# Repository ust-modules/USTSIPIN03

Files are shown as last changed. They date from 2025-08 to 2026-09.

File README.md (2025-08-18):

## USTSIPIN03 - Semiconductor-based ionizing radiation dosimeter and spectrometer analog front-end

The USTSIPIN03 is developed as a single-board improved variant of the [PIND02](https://github.com/mlab-modules/PIND02) and [PCRD07](https://github.com/mlab-modules/PCRD07) modules from the [MLAB.cz development system](https://www.mlab.cz/). The analog front-end is the sensing component of the [AIRDOS04 cosmic radiation detector and dosimeter](https://docs.dos.ust.cz/airdos/AIRDOS04).

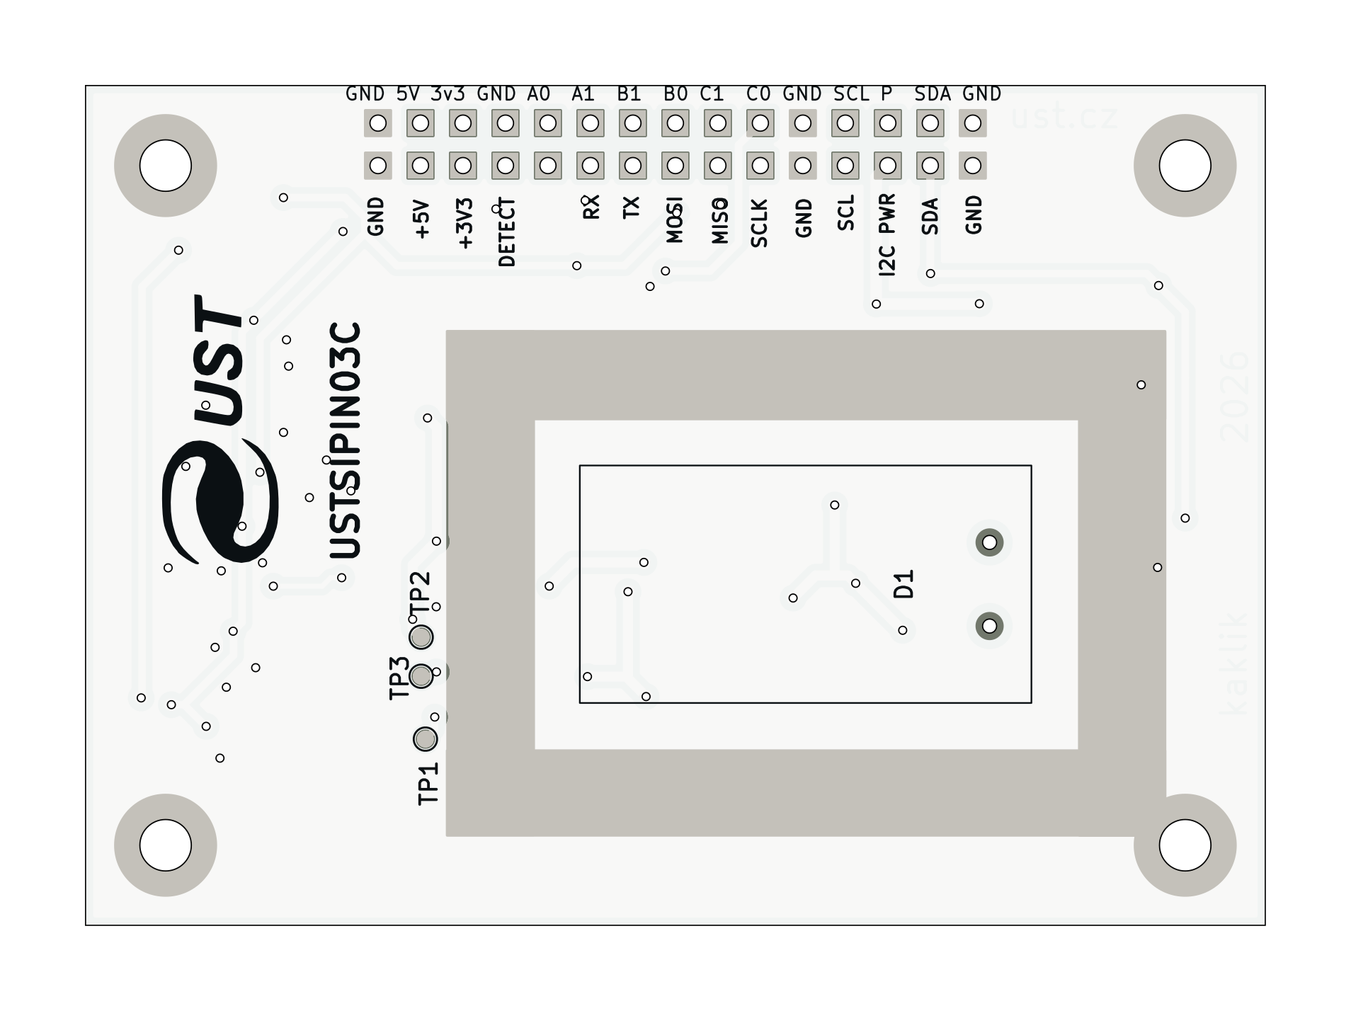
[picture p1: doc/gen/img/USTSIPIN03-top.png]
USTSIPIN03 Top view


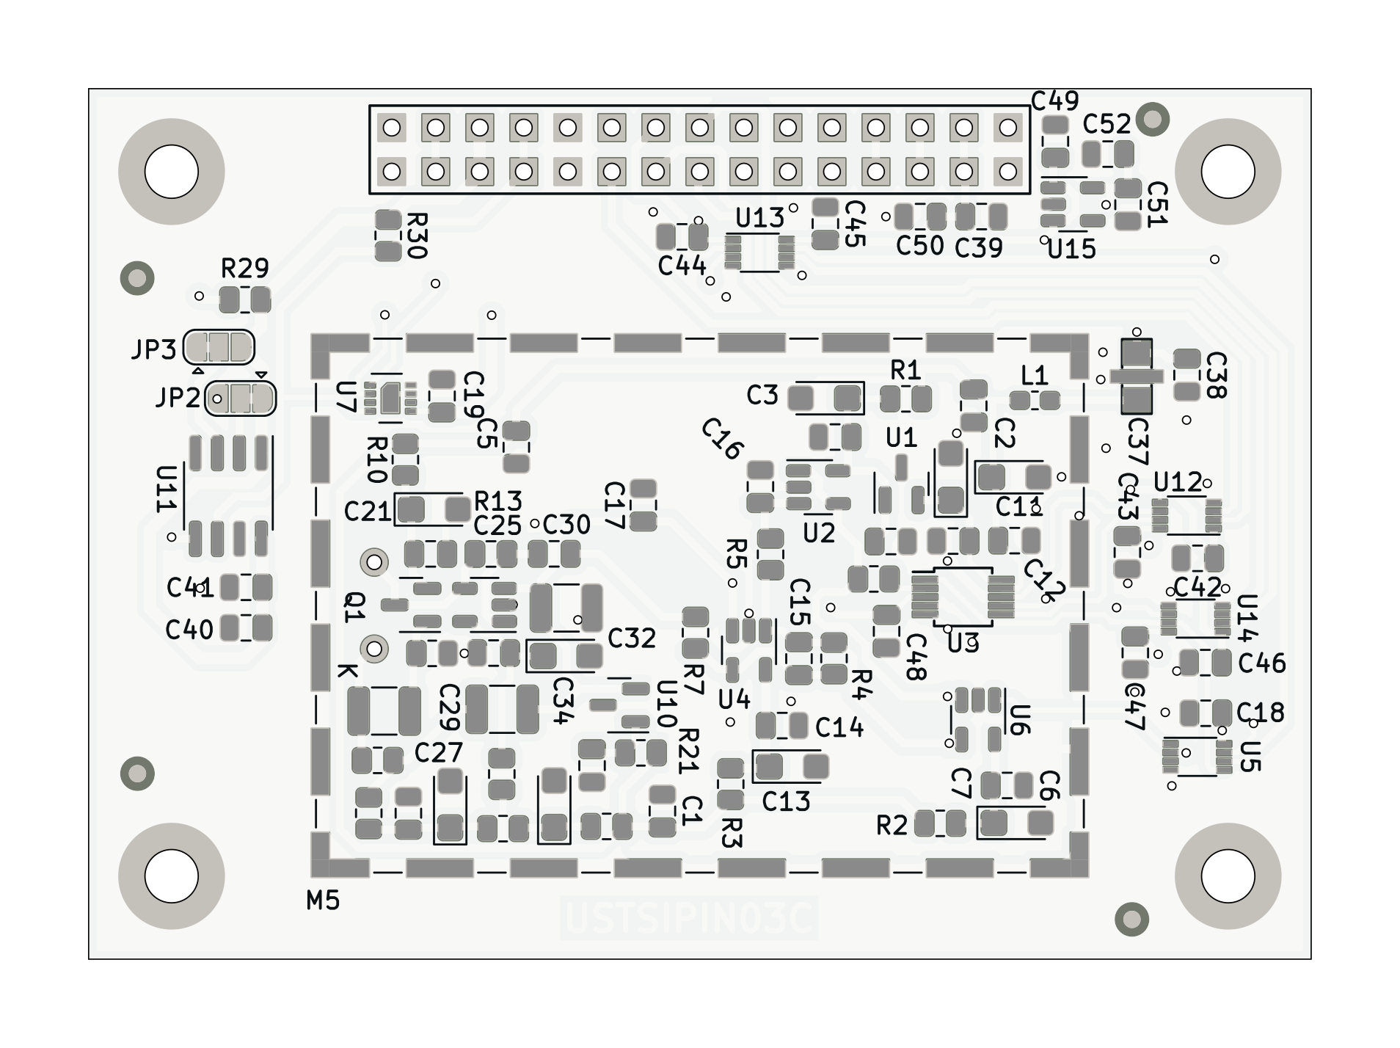
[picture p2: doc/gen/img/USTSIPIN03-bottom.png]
USTSIPIN03 Bottom view


### Features

* High-sensitivity silicon semiconductor PIN diode detector front-end
* Low-noise analog signal chain optimized for wide-energy radiation detection
* Designed for spectrometric and dosimetric measurements
* Suitable for connection to system MCU or FPGA via SPI interface
* Auxiliary I2C interface for service and calibration data access

### Electrical and Interface Specifications

* **Power supply**: +5 V DC
* **Maximum power consumption**: 5.5 mA (28 mW)
* **Main data interface**: SPI with up to 15 MHz system clock
* **Service interface**: I2C with access to
    * Temperature and humidity sensors
    * Unique serial number
    * Calibration memory
* Dimensions: 70.65 x 50.3 x 10 mm
* Mass: 24 g (including connector) 

AIRDOS04 Sensor Top

AIRDOS04 Sensor Bottom

### Measurement Specifications

* **Detection element**: Silicon PIN diode, volume 44 mm³
* **Effective number of energy channels**: ~65000
* **Deposited energy range**: 40 keV to 80 MeV
* **Spectral resolution**: 15 ±2 keV
* **Maximum sampling rate**: 250 kHz
* **Measurement modes**:
  * Pulse counting
  * Deposited energy spectroscopy
  * Dose rate estimation

### Applications

* Cosmic ray detection
* Environmental radiation monitoring
* Portable dosimetry systems
* Radiation protection systems
  
### Related Projects

* [AIRDOS04](https://github.com/UniversalScientificTechnologies/AIRDOS04) - Complete radiation detection system based on USTSIPIN03
* [PIND02](https://github.com/mlab-modules/PIND02) - Predecessor MLAB module
* [PCRD07](https://github.com/mlab-modules/PCRD07) - Related MLAB analog front-end module

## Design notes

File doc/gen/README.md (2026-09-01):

# PCB

Board size: 70.61x50.29 mm (2.78x1.98 inches)

- This is the size of the rectangle that contains the board
- Thickness: 1.6 mm (63 mils)
- Material: FR4
- Finish: HAL SnPb
- Layers: 2
- Copper thickness: 35 µm

Solder mask: TOP / BOTTOM

- Color: Green

Silk screen: TOP / BOTTOM

- Color: White

Stackup:

| Name                 | Type                 | Color            | Thickness [µm]| Material        | Er        | Loss tan     |
|----------------------|----------------------|------------------|---------------|-----------------|-----------|--------------|
| F.SilkS              | Top Silk Screen      |                  |               |                 |           |              |
| F.Mask               | Top Solder Mask      |                  |            10 |                 |           |              |
| F.Cu                 | copper               |                  |            35 |                 |           |              |
| dielectric 1         | core                 |                  |          1510 | FR4             |       4.5 |        0.020 |
| B.Cu                 | copper               |                  |            35 |                 |           |              |
| B.Mask               | Bottom Solder Mask   |                  |            10 |                 |           |              |
| B.Paste              | Bottom Solder Paste  |                  |               |                 |           |              |
| B.SilkS              | Bottom Silk Screen   |                  |               |                 |           |              |

# Important sizes

Clearance: 0.2 mm (8 mils)

Track width: 0.2 mm (8 mils)

- By design rules: 0.2 mm (8 mils)

Drill: 0.5 mm (20 mils)

- Vias: 0.5 mm (20 mils) [Design: 0.4 mm (16 mils)]
- Pads: 0.85 mm (33 mils)
- The above values are real drill sizes, they add 0.1 mm (4 mils) to plated holes (PTH)

Via: 0.8/0.4 mm (31/16 mils)

- By design rules: 0.8/0.3 mm (31/12 mils)
- Micro via: yes [0.2/0.1 mm (8/4 mils)]
- Buried/blind via: yes
- Total: 56 (thru: 56 buried/blind: 0 micro: 0)

Outer Annular Ring: 0.15 mm (6 mils)

- By design rules: 0.26 mm (10 mils)

Eurocircuits class: 4B
- Using min drill 0.5 mm for an OAR of 0.15 mm

# General stats

Components count: (SMD/THT)

- Top: 0/6 (THT)
- Bottom: 87/1 (SMD + THT)

Defined tracks:

- 0.2 mm (8 mils)
- 0.3 mm (12 mils)
- 0.4 mm (16 mils)
- 0.5 mm (20 mils)
- 0.6 mm (24 mils)
- 0.7 mm (28 mils)
- 0.8 mm (31 mils)

Used tracks:

- 0.2 mm (8 mils) (2) defined: yes
- 0.3 mm (12 mils) (136) defined: yes
- 0.4 mm (16 mils) (59) defined: yes
- 0.45 mm (18 mils) (415) defined: no
- 0.5 mm (20 mils) (4) defined: yes
- 0.6 mm (24 mils) (21) defined: yes
- 0.7 mm (28 mils) (37) defined: yes

Defined vias:

Used vias:

- 0.8/0.4 mm (31/16 mils) (Count: 56, Aspect: 2.0 A) defined: no

Holes (excluding vias):

- 0.76 mm (30 mils) (2)
- 0.89 mm (35 mils) (30)
- 3.0 mm (118 mils) (4)

Oval holes:

Drill tools (including vias and computing adjusts and rounding):

- 0.5 mm (20 mils) (56)
- 0.85 mm (33 mils) (2)
- 1.0 mm (39 mils) (30)
- 3.1 mm (122 mils) (4)

Solder paste stats:

Using a paste with 87.75 % alloy, that has an specific gravity for the alloy of 7.4 g/cm³
and 1.0 g/cm³ for the flux. This paste has an specific gravity of  4.15 g/cm³.

The stencil thickness is  0.12 mm.

| Side   | Pads with paste | Area [mm²] | Paste [g] |
|--------|-----------------|------------|-----------|
| Total  |             260 |     352.17 |      1.75 |

Note: this is just an approximation to the theoretical value. Margins of the solder mask and waste aren't computed.

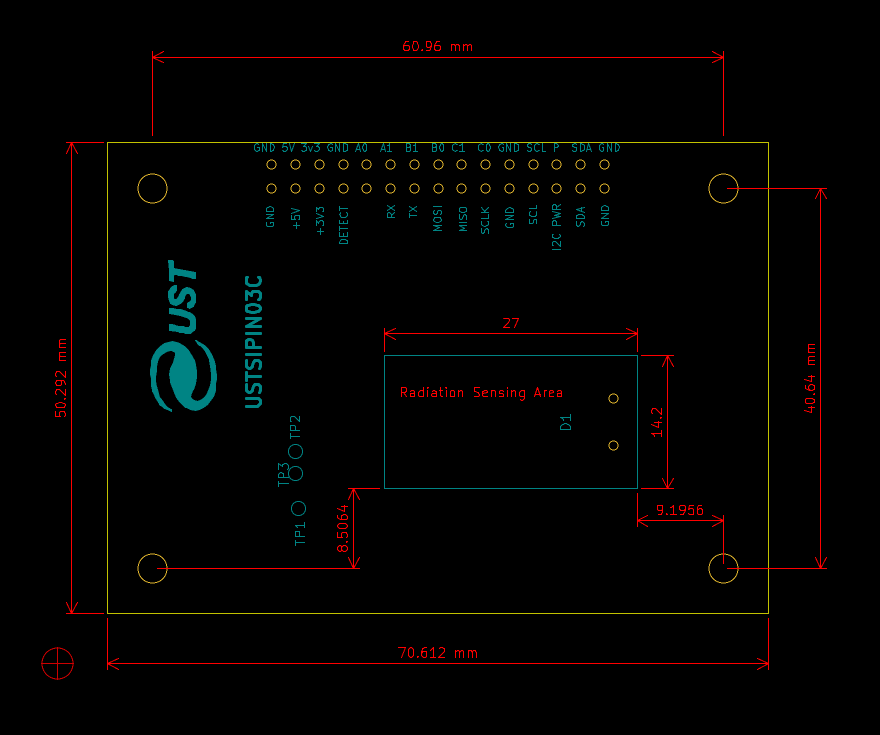
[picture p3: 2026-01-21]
doc/img/AIRDOS04_dimensions.png

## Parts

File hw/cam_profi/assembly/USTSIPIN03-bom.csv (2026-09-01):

Component | Description | Part | References | Value | Footprint | Quantity Per PCB | Datasheet | ust_id | ust_id2
1 | Unpolarized capacitor | C | C25 | 1pF | C_0805_2012Metric | 1 |  | 5c70984712875079b91f8b9f
2 | Unpolarized capacitor | C | C16C48 | 1nF | C_0805_2012Metric | 2 |  | 5c70984812875079b91f8ba6
3 | Unpolarized capacitor | C | C15 | 3n3 | C_0805_2012Metric | 1 |  | 651abc26462c6d9e720551fa
4 | Unpolarized capacitor, small symbol | C_Small | C1C2C4C5C7C8C10C12C14C17C18C19C20C28C30C33C36C38C41C42C43C44C45C46C47C50C52 | 100nF | C_0805_2012Metric | 27 |  | 5c70984712875079b91f8b4c 6508260b462c6d9e720541f1
5 | Unpolarized capacitor | C | C22C29C32 | 1uF | C_1210_3225Metric | 3 |  | 65082f52462c6d9e72054238
6 | EMI filter, single capacitor | Filter_EMI_C | C37 | 1uF | FIR_0805 | 1 | http://www.murata.com/~/media/webrenewal/support/library/catalog/products/emc/emifil/c31e.ashx?la=en-gb | 5c70984412875079b91f880f
7 | Polarized capacitor | C_Polarized | C3C6C9C11C13 | 10uF | CP_EIA-3216-18_Kemet-A | 5 |  | 65089dd0462c6d9e720542b3
8 | Polarized capacitor, small symbol | C_Polarized_Small | C21C26C27C34 | 10uF | CP_EIA-3216-18_Kemet-A | 4 | https://eu.mouser.com/datasheet/2/40/TAJ-3165264.pdf | 65089dd0462c6d9e720542b3
9 | Unpolarized capacitor | C | C39C40C49C51 | 10uF | C_0805_2012Metric | 4 |  | 5c70984712875079b91f8b53
10 | Photodiode | D_Photo | D1 | S2744-09 | HAMAMATSU_S2744-09 | 1 | https://www.hamamatsu.com/content/dam/hamamatsu-photonics/sites/documents/99_SALES_LIBRARY/ssd/s2744-08_etc_kpin1049e.pdf | 628d118cdc56076e9a2235e4
11 | 2x15 2.54 mm pitch header | HEADER_2x15 | J1 | HEADER_2x15 | Straight_2x15 | 1
12 | Inductor with ferrite core, small symbol | L_Ferrite_Small | L1 | NL03KT330 | L_0603_1608Metric_Pad1.05x0.95mm_HandSolder | 1 |  | 64fe1808f3b9d36f37fc944d
13 | Two-piece EMI RF shielding cabinet | RFShield_TwoPieces | M5 | RFShield_TwoPieces | Laird_Technologies_BMI-S-210-F_44.00x30.50mm | 1 |  | 5c70984312875079b91f873d | 5c70984312875079b91f873c
14 | N-JFET transistor, source/drain/gate | Q_NJFET_SDG | Q1 | 2SK2394-6 | SOT-23 | 1 |  | 628d134fdc56076e9a223625
15 | Resistor | R | R6 | 10 | R_0805_2012Metric | 1 |  | 5c70984512875079b91f896d
16 | Resistor | R | R1R2R3 | 100 | R_0805_2012Metric | 3 |  | 5c70984512875079b91f8977
17 | Resistor | R | R10R19R21 | 470R | R_0805_2012Metric | 3 |  | 5c70984512875079b91f8986
18 | Resistor | R | R7 | 1k | R_0805_2012Metric | 1 |  | 5c70984512875079b91f898c
19 | Resistor | R | R12R14R15R16R17 | 4k7 | R_0805_2012Metric | 5 |  | 5c70984612875079b91f8995
20 | Resistor | R | R4R5R29R30 | 10k | R_0805_2012Metric | 4 |  | 5c70984612875079b91f899f
21 | Resistor | R | R13 | 10M | R_0805_2012Metric | 1 |  | 5c70984712875079b91f8aae
22 | Single Rail-to-Rail High Output Current Operational Amplifiers, SOT-23-5 | AD8691 | U2U4 | AD8691 | TSOT-23-5 | 2 | https://www.analog.com/media/en/technical-documentation/data-sheets/AD8691_8692_8694.pdf | 5d47c084128750448e6b4671
23 | I2C Serial EEPROM, 64Kb (8192x8) with Unique Serial Number, SO8 | AT24CS64-SSHM | U11 | AT24CS64-SSHM | SOIC-8_3.9x4.9mm_P1.27mm | 1 | http://ww1.microchip.com/downloads/en/DeviceDoc/Atmel-8870-SEEPROM-AT24CS64-Datasheet.pdf | 5c70984712875079b91f8b99
24 | 2.0V 25μA Micropower Voltage Reference, SOT-23 | ISL21070CIH320Z-TK | U1 | ISL21080CIH341Z-TK | SOT-23 | 1 | https://cz.mouser.com/datasheet/2/698/REN_isl21080_DST_20040119-1998038.pdf | 6555591d0c8d609e3e79abc1
25 | 2.0V 25μA Micropower Voltage Reference, SOT-23 | ISL21070CIH320Z-TK | U10 | ISL21080DIH309 | SOT-23 | 1 | https://www.renesas.com/us/en/document/dst/isl21080-datasheet | 5c70984712875079b91f8b0b
26 | Dual channel 16-bit SAR Analog to Digital Converter, 5V supply, 150ksps, SPI interface | LTC1865-MS | U3 | LTC1865-MS | MSOP-10_3x3mm_P0.5mm | 1 | https://www.analog.com/media/en/technical-documentation/data-sheets/18645fb.pdf | 67f14385ee7fc534862c535e
27 | 300mA Low-dropout Voltage Regulator, Vout 3.3V, Vin up to 5.5V, SOT-23 | MIC5504-3.3YM5 | U15 | MIC5504-3.3YM5-TR | SOT-23-5 | 1 | http://ww1.microchip.com/downloads/en/DeviceDoc/MIC550X.pdf | 5c7255e81287500b4e112ea2
28 |  | OPA314 | U8 | OPA314 | SOT-23-5 | 1 | https://www.ti.com/lit/ds/symlink/opa314.pdf | 5c70984412875079b91f879a
29 | I²C humidity and temperature sensor, ±2%RH, ±0.2°C, DFN-8 | SHT31-DIS | U7 | SHT31-DIS | Sensirion_DFN-8-1EP_2.5x2.5mm_P0.5mm_EP1.1x1.7mm | 1 | https://sensirion.com/media/documents/213E6A3B/63A5A569/Datasheet_SHT3x_DIS.pdf | 5c70984612875079b91f89e4
30 | 74AUC1G74, Single D Flip-Flop, Low-Voltage CMOS | 74LVC2G74 | U5 | SN74LVC2G74 | VSSOP-8_2.3x2mm_P0.5mm | 1 | https://www.ti.com/lit/ds/symlink/sn74lvc2g74-ep.pdf | 65555d4795a79cc5ac409b41
31 | Dual supply translating transceiver, 3-state, 2-bit, VSSOP-8 | 74LVC2T45DC | U12U13U14 | SN74LVC2T45DCU | VSSOP-8_2.3x2mm_P0.5mm | 3 | https://assets.nexperia.com/documents/data-sheet/74LVC_LVCH2T45.pdf | 65555a850c8d609e3e79abde
32 | Single Rail-to-Rail High Output Current Operational Amplifiers, SOT-23-5 | AD8691 | U6 | TS3021ILT | SOT-23-5 | 1 | https://www.st.com/resource/en/datasheet/ts3021.pdf | 5d47bfd4128750448e6b465e

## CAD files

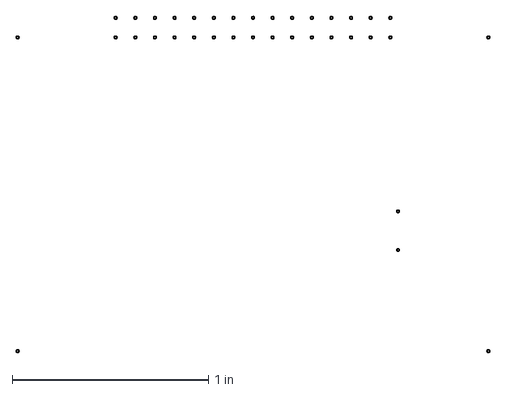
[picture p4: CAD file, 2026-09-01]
doc/gen/dxf/USTSIPIN03-User_Drawings.dxf
2.41 x 1.71 in

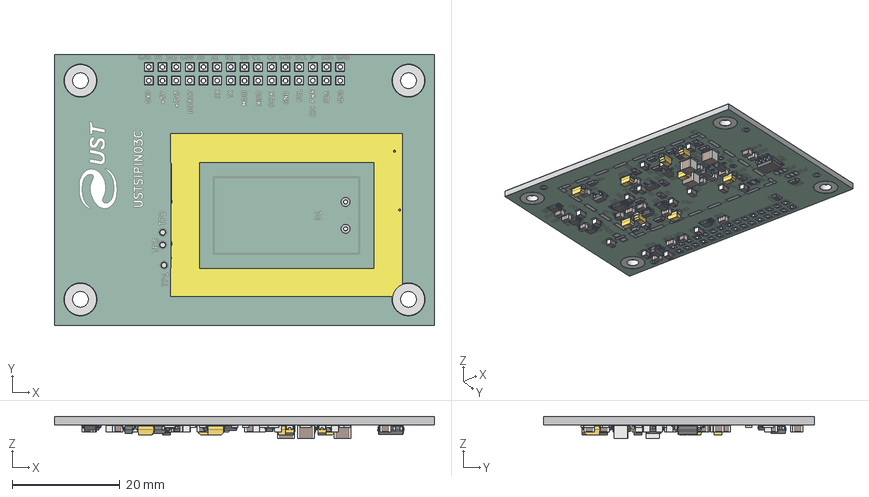
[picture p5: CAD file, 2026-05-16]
doc/gen/mesh/USTSIPIN03.step
70.6 x 50.3 x 4.17 mm
C_0805_2012Metric x 35
TSOT-23-5 x 2
CP_EIA-3216-18_Kemet-A x 9
R_0805_2012Metric x 18
SOT-23-5 x 3
C_1210_3225Metric x 3
VSSOP-8_2.3x2mm_P0.5mm x 4
MSOP-10_3x3mm_P0.5mm
SOT-23 x 3
L_0603_1608Metric
SOIC-8_3.9x4.9mm_P1.27mm
kibot_3cg9ln61_copper
kibot_3cg9ln61_pad
kibot_3cg9ln61_via
kibot_3cg9ln61_silkscreen x 2
kibot_3cg9ln61_soldermask x 2
kibot_3cg9ln61_PCB

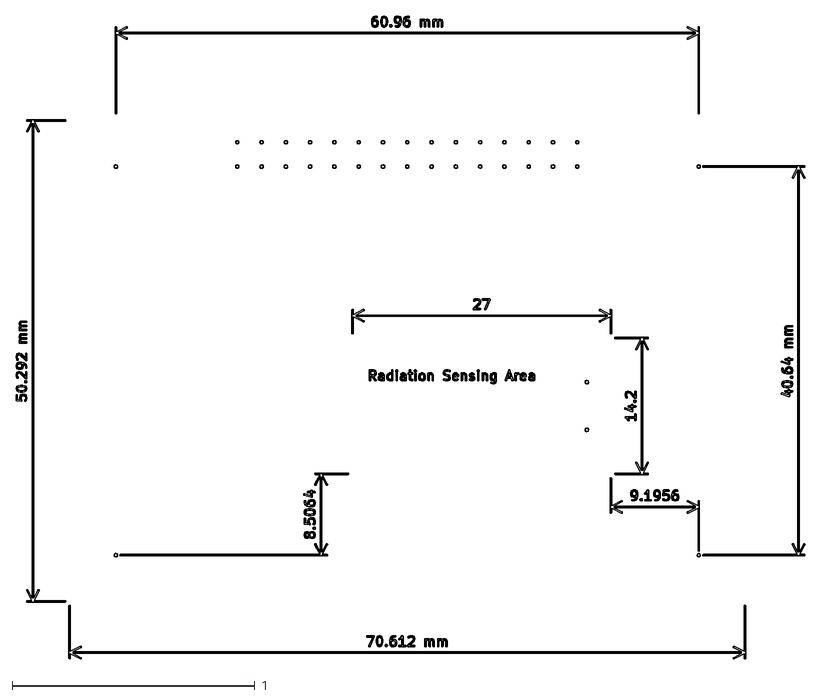
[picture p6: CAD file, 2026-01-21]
doc/gen/USTSIPIN03/dxf/USTSIPIN03-User_Comments.dxf
3.25 x 2.65

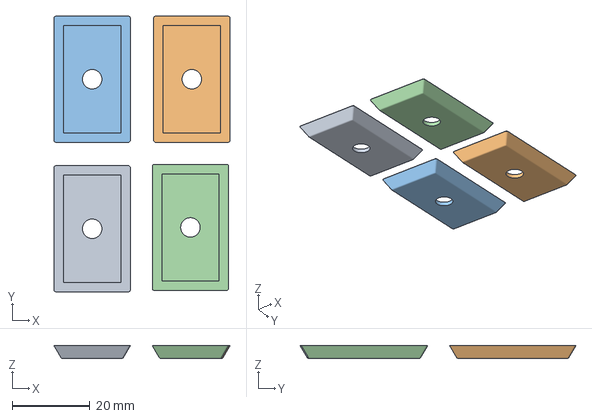
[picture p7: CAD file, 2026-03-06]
hw/cad/sensor_frame.3mf
45.2 x 70.8 x 3.32 mm

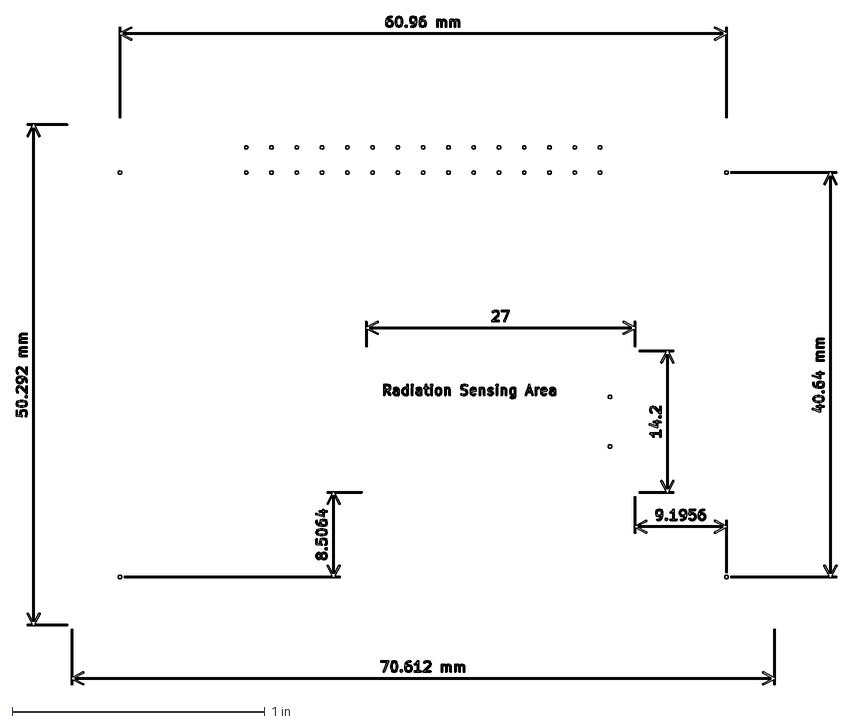
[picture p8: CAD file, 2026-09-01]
doc/gen/dxf/USTSIPIN03-User_Comments.dxf
3.25 x 2.65 in

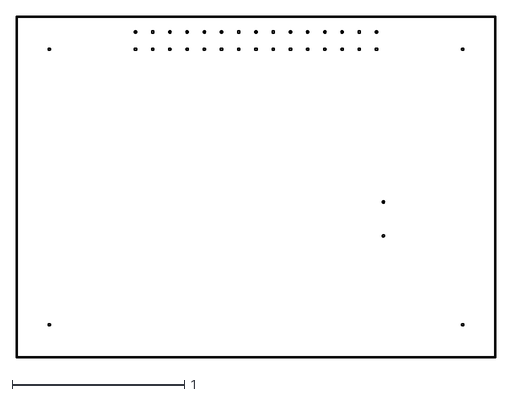
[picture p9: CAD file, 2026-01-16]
doc/gen/USTSIPIN03/dxf/USTSIPIN03-Edge_Cuts.dxf
2.79 x 1.99

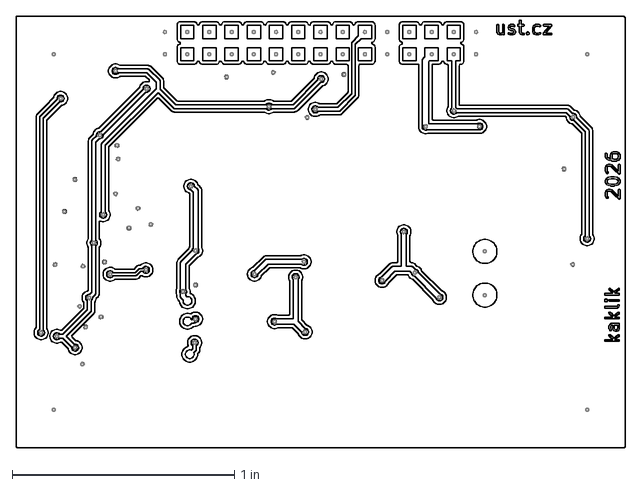
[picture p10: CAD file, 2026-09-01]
doc/gen/dxf/USTSIPIN03-F_Cu.dxf
2.74 x 1.94 in

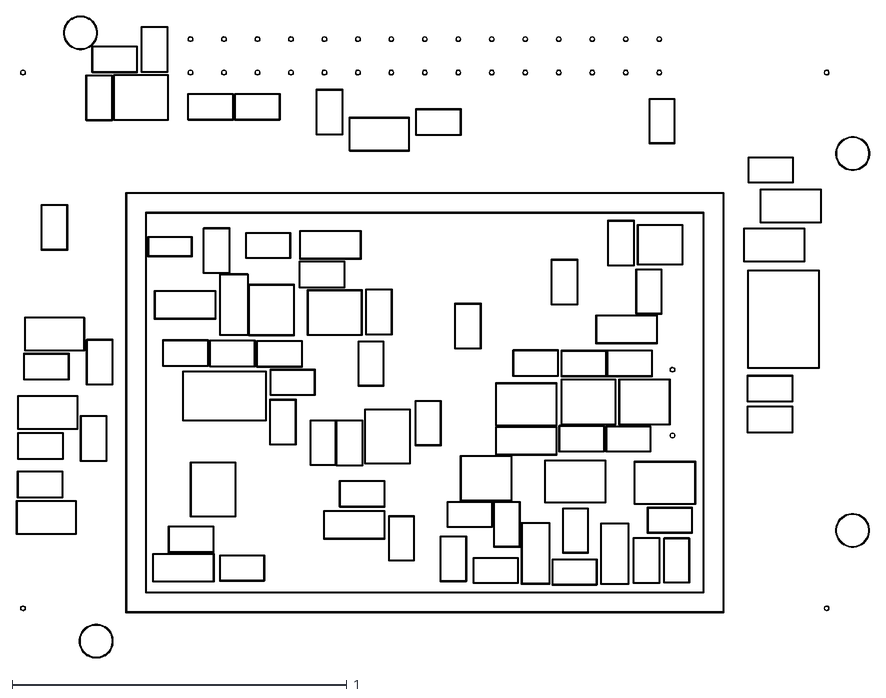
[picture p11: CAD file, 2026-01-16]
doc/gen/USTSIPIN03/dxf/USTSIPIN03-B_Courtyard.dxf
2.55 x 1.92

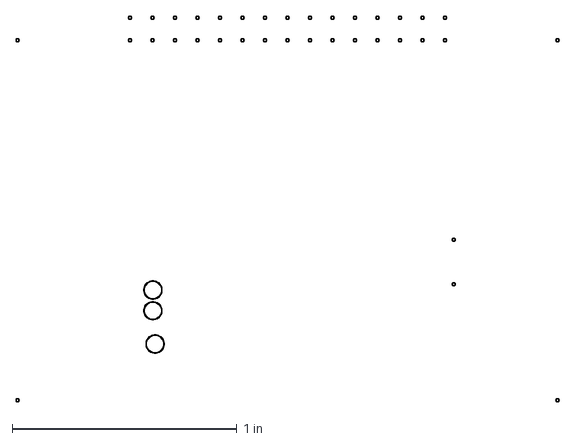
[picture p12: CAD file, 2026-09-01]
doc/gen/dxf/USTSIPIN03-F_Courtyard.dxf
2.41 x 1.71 in

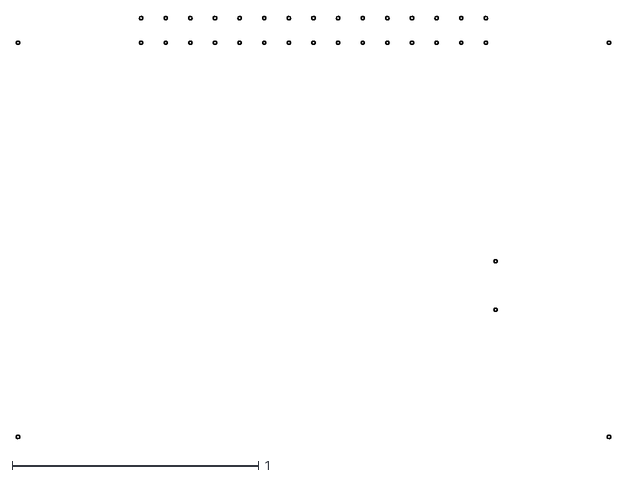
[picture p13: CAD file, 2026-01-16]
doc/gen/USTSIPIN03/dxf/USTSIPIN03-Margin.dxf
2.41 x 1.71

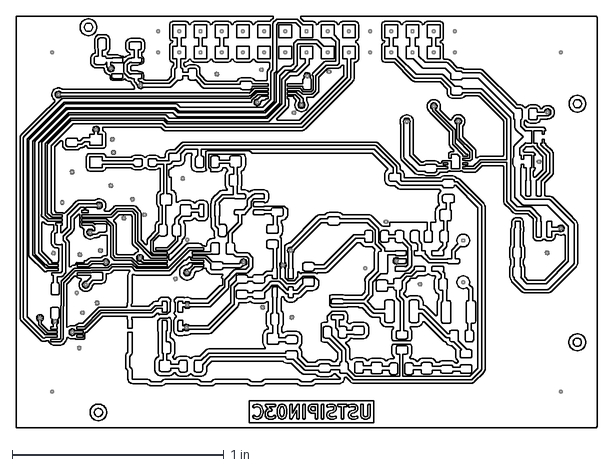
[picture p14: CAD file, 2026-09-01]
doc/gen/dxf/USTSIPIN03-B_Cu.dxf
2.74 x 1.94 in

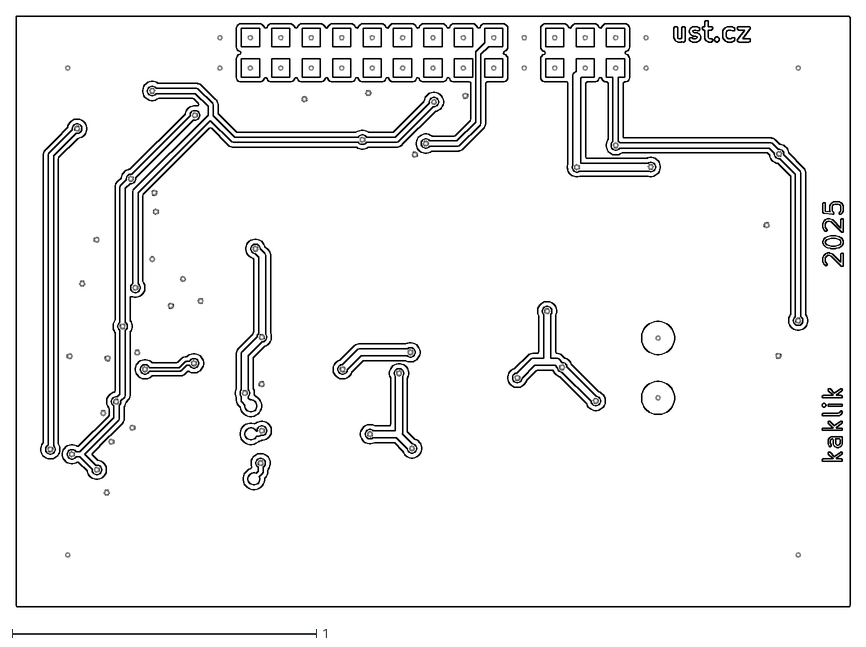
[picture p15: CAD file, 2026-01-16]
doc/gen/USTSIPIN03/dxf/USTSIPIN03-F_Cu.dxf
2.74 x 1.94

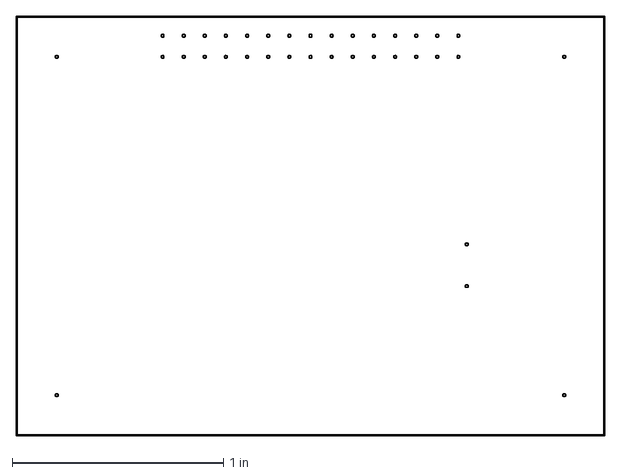
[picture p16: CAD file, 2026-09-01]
doc/gen/dxf/USTSIPIN03-Edge_Cuts.dxf
2.79 x 1.99 in

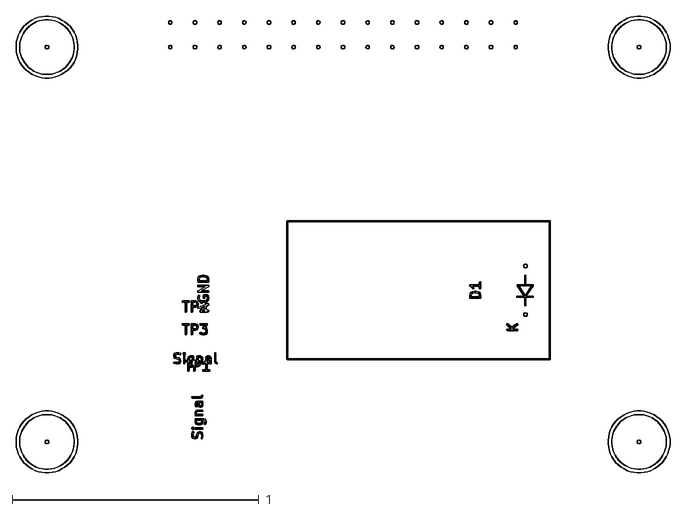
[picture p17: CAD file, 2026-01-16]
doc/gen/USTSIPIN03/dxf/USTSIPIN03-F_Fab.dxf
2.65 x 1.85

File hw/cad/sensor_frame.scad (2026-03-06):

$fn=100;
clearance = 0.5;

sensor_width = 14.2;
sensor_lenght = 27.0;
sensor_height = 2.2;
layer_thickness = 0.3; 

module sensor_frame(){
  difference(){
      hull(){
        translate([0,0,5*layer_thickness])
          minkowski(){
            cube([sensor_width + 2*clearance, sensor_lenght+ 2*clearance, sensor_height-4*clearance + layer_thickness],center=true);
            sphere(r = clearance);
          }
        translate([0,0,-sensor_height/2 + clearance/20])
          minkowski(){
            cube([sensor_width + 2*sensor_height, sensor_lenght + 2*sensor_height, clearance/10], center=true);
            translate([0,0,clearance/20]) cylinder(r = clearance, h = clearance/10);
          }
      }
      cube([sensor_width + clearance, sensor_lenght + clearance, sensor_height],center=true);
      cylinder(h=2*sensor_height, d=5,center=false);
  }
}

sensor_frame();

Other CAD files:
doc/gen/USTSIPIN03/mesh/USTSIPIN03.step
doc/gen/USTSIPIN03/dxf/USTSIPIN03-B_Fab.dxf
doc/gen/dxf/USTSIPIN03-F_Fab.dxf
doc/gen/USTSIPIN03/dxf/USTSIPIN03-B_Cu.dxf
doc/gen/USTSIPIN03/dxf/USTSIPIN03-B_Mask.dxf
doc/gen/USTSIPIN03/dxf/USTSIPIN03-B_Paste.dxf
doc/gen/USTSIPIN03/dxf/USTSIPIN03-B_Silkscreen.dxf
doc/gen/USTSIPIN03/dxf/USTSIPIN03-F_Courtyard.dxf
doc/gen/USTSIPIN03/dxf/USTSIPIN03-F_Mask.dxf
doc/gen/USTSIPIN03/dxf/USTSIPIN03-F_Silkscreen.dxf
doc/gen/dxf/USTSIPIN03-B_Courtyard.dxf
doc/gen/dxf/USTSIPIN03-B_Fab.dxf
doc/gen/dxf/USTSIPIN03-B_Mask.dxf
doc/gen/dxf/USTSIPIN03-B_Paste.dxf
doc/gen/dxf/USTSIPIN03-B_Silkscreen.dxf
doc/gen/dxf/USTSIPIN03-F_Mask.dxf
doc/gen/dxf/USTSIPIN03-F_Silkscreen.dxf
doc/gen/mesh/USTSIPIN03.stl
hw/cad/sensor_frame.stl

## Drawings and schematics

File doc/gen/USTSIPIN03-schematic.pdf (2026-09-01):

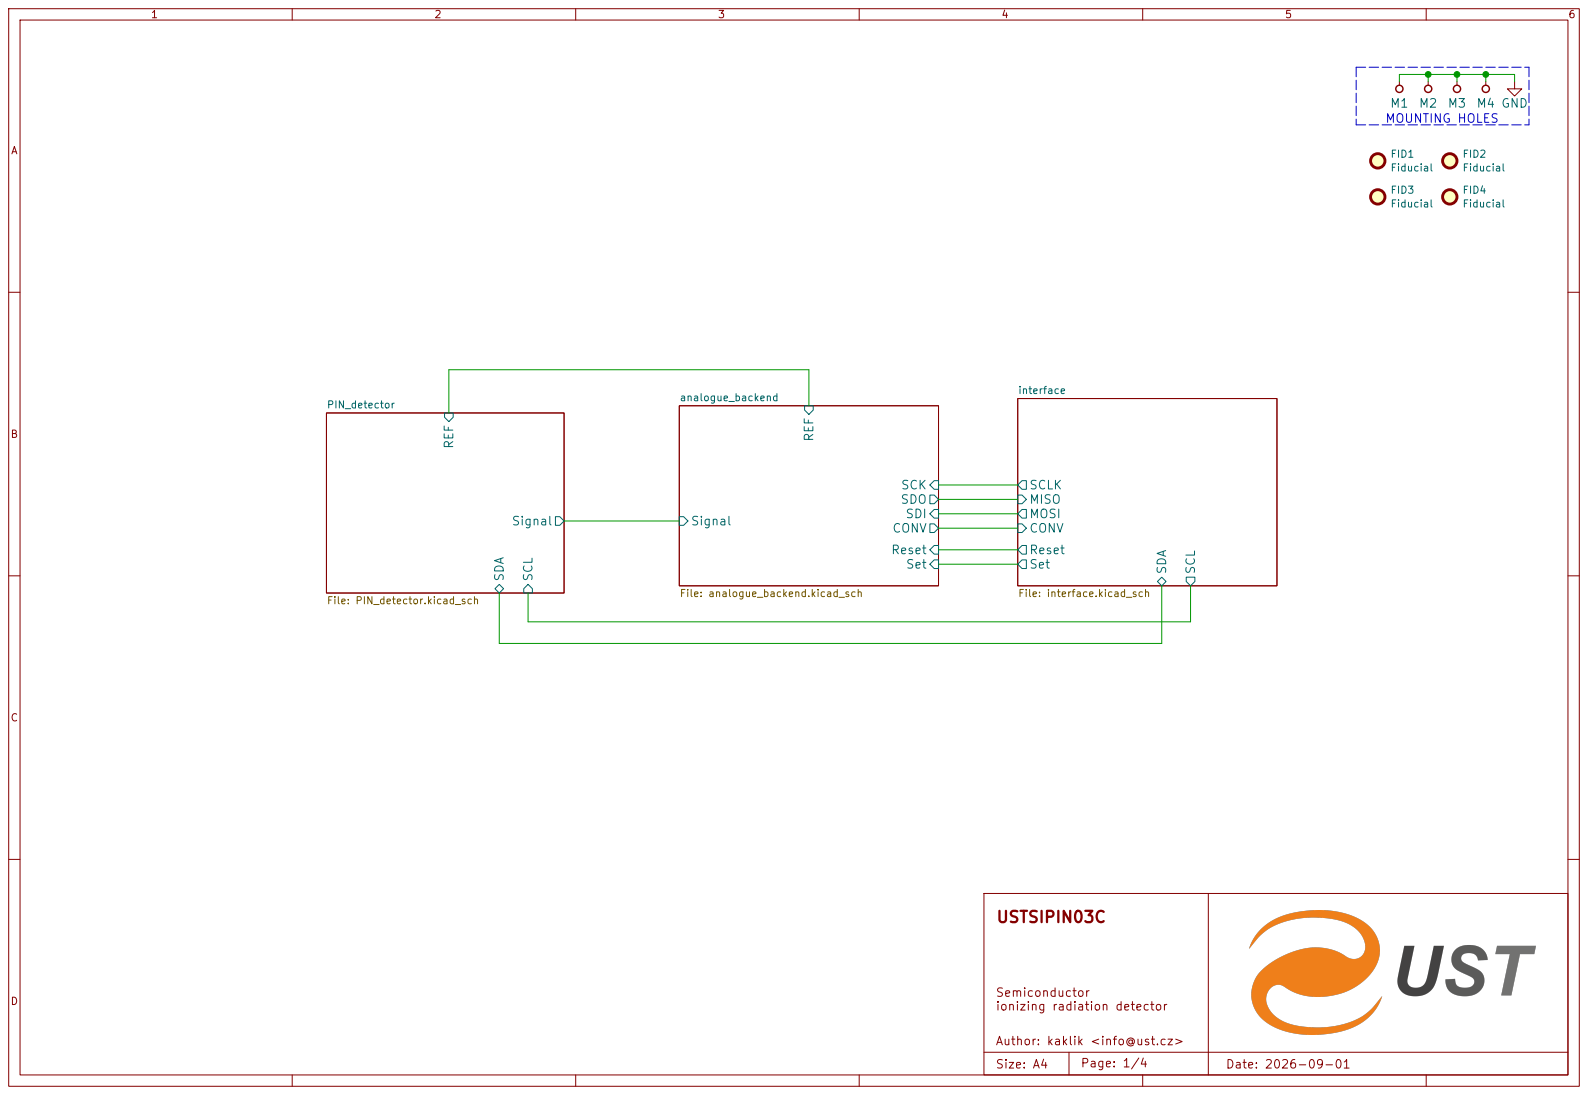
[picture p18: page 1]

USTSIPIN03C Semiconductor ionizing radiation detector Author: kaklik <info@ust.cz>

Size: A4 | Page: 1/4 | Date: 2026-09-01

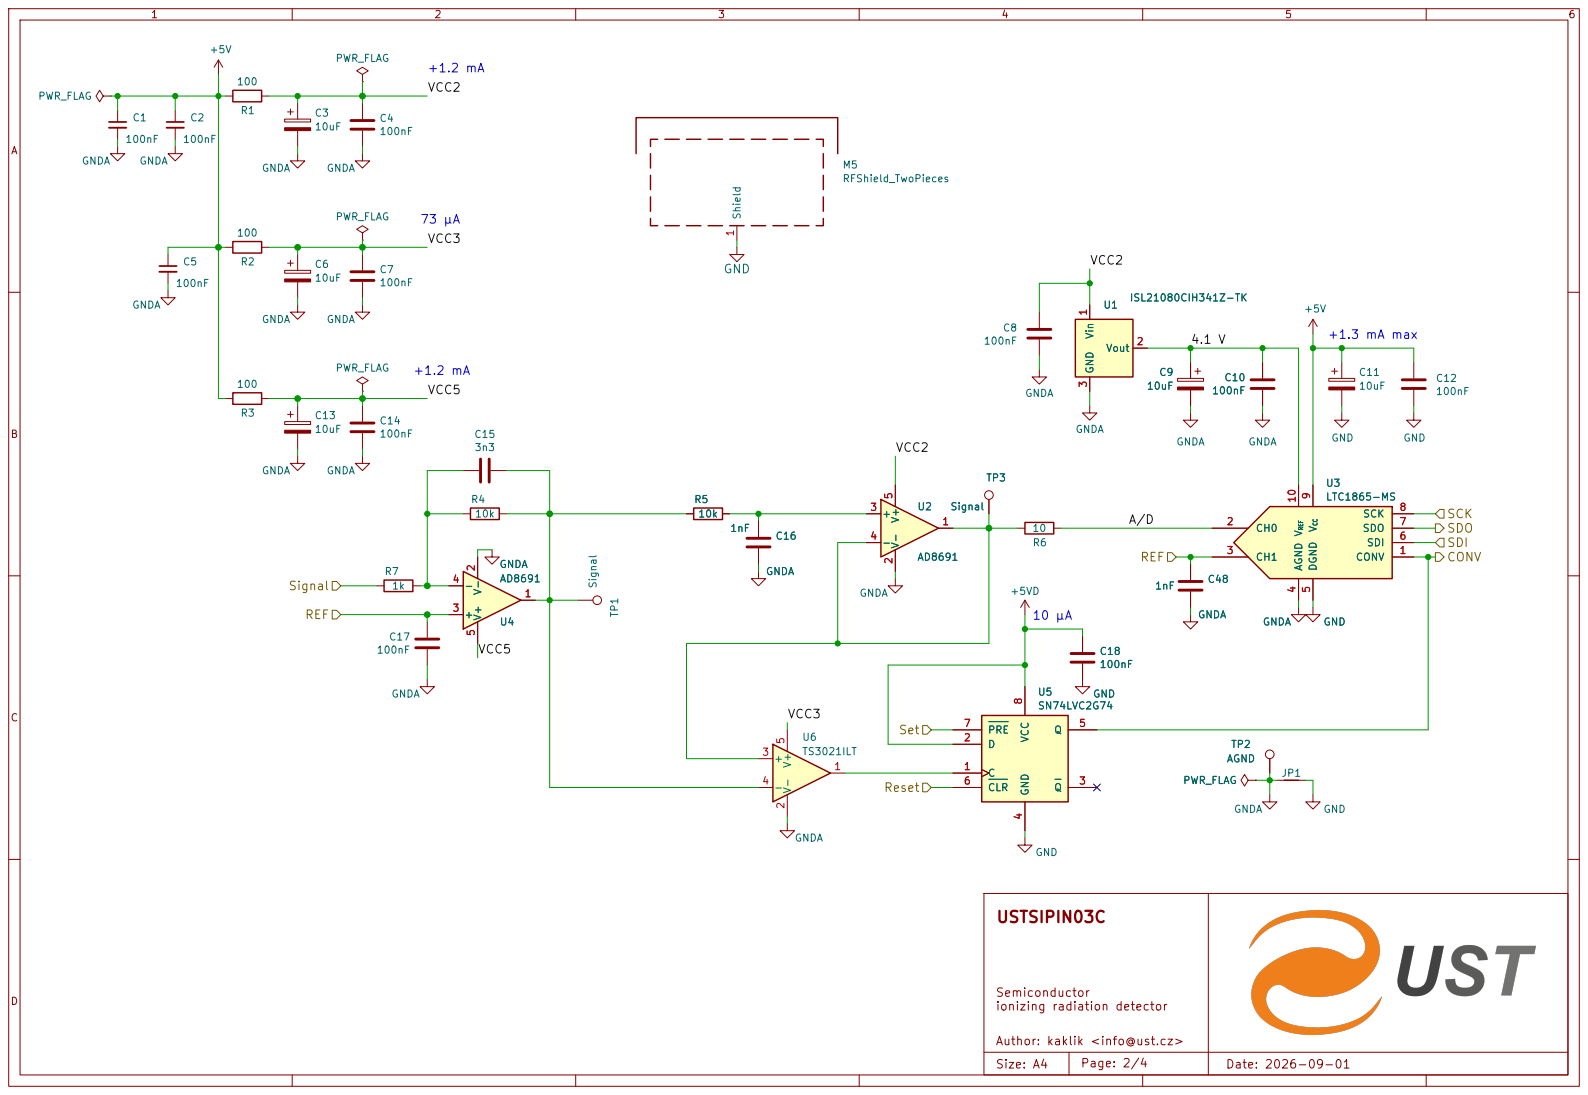
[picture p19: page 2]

USTSIPIN03C Semiconductor ionizing radiation detector Author: kaklik <info@ust.cz>

Size: A4 | Page: 2/4 | Date: 2026-09-01

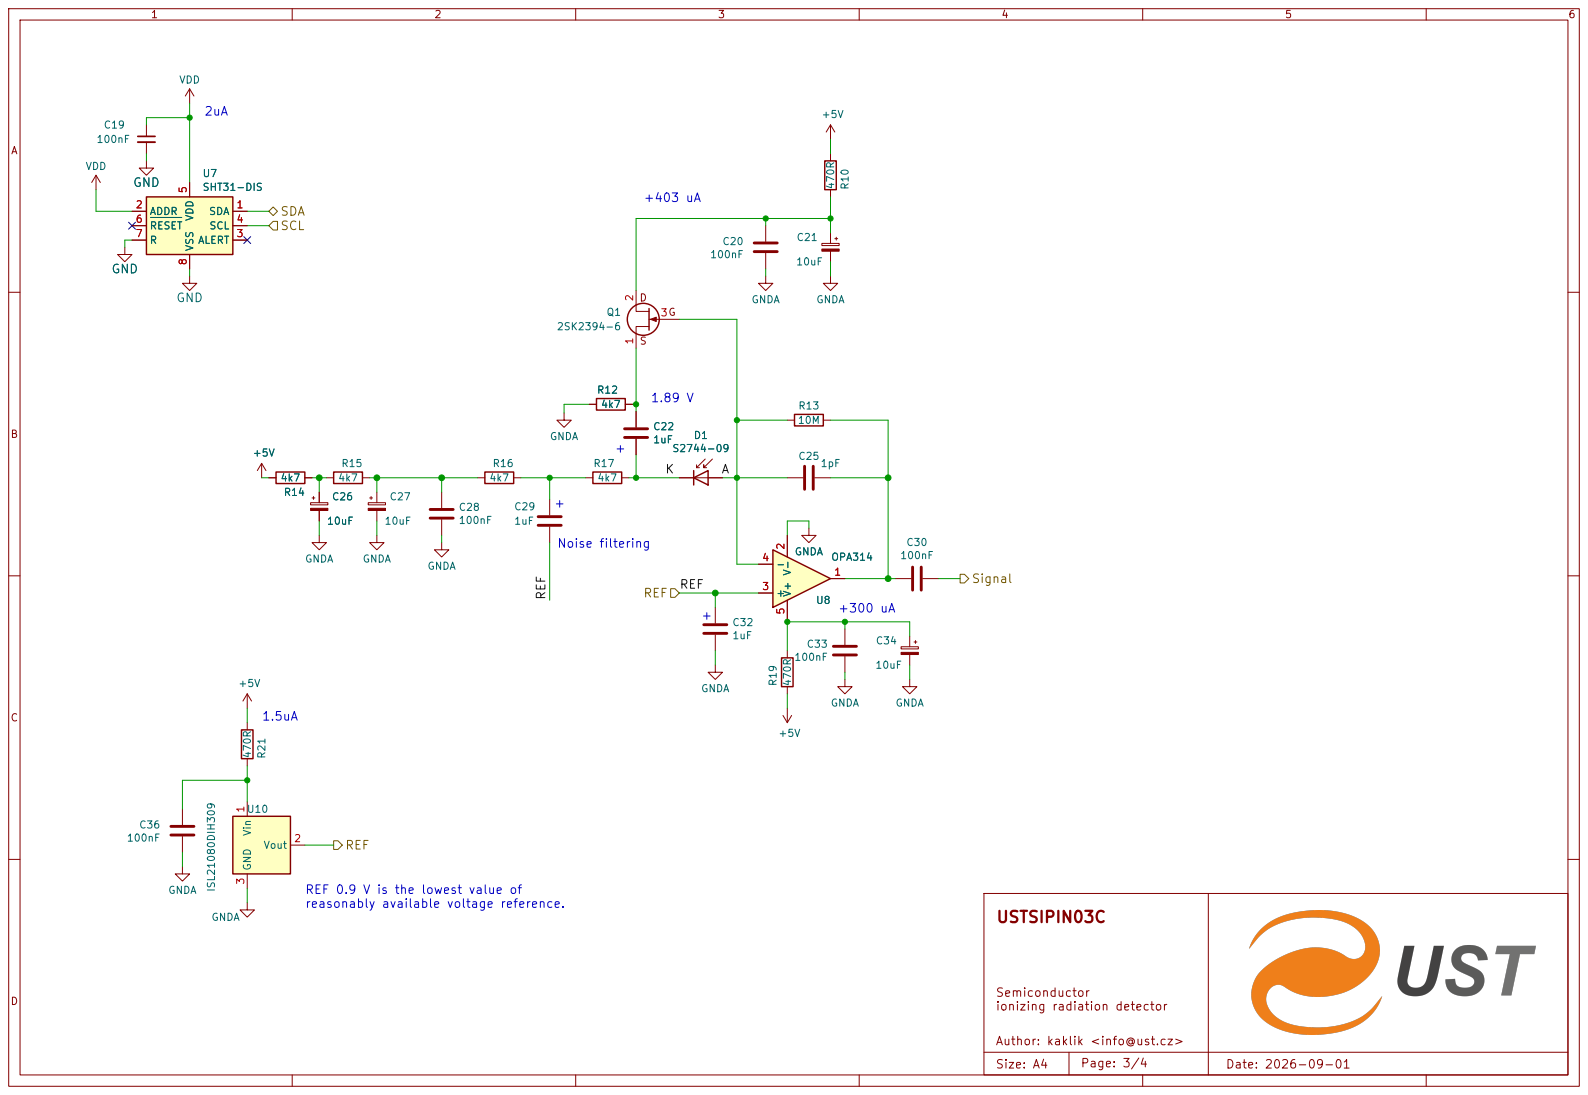
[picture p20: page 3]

REF 0.9 V is the lowest value of
reasonably available voltage reference.

USTSIPIN03C Semiconductor Author: kaklik <info@ust.cz>

Size: A4 | Page: 3/4 | Date: 2026-09-01

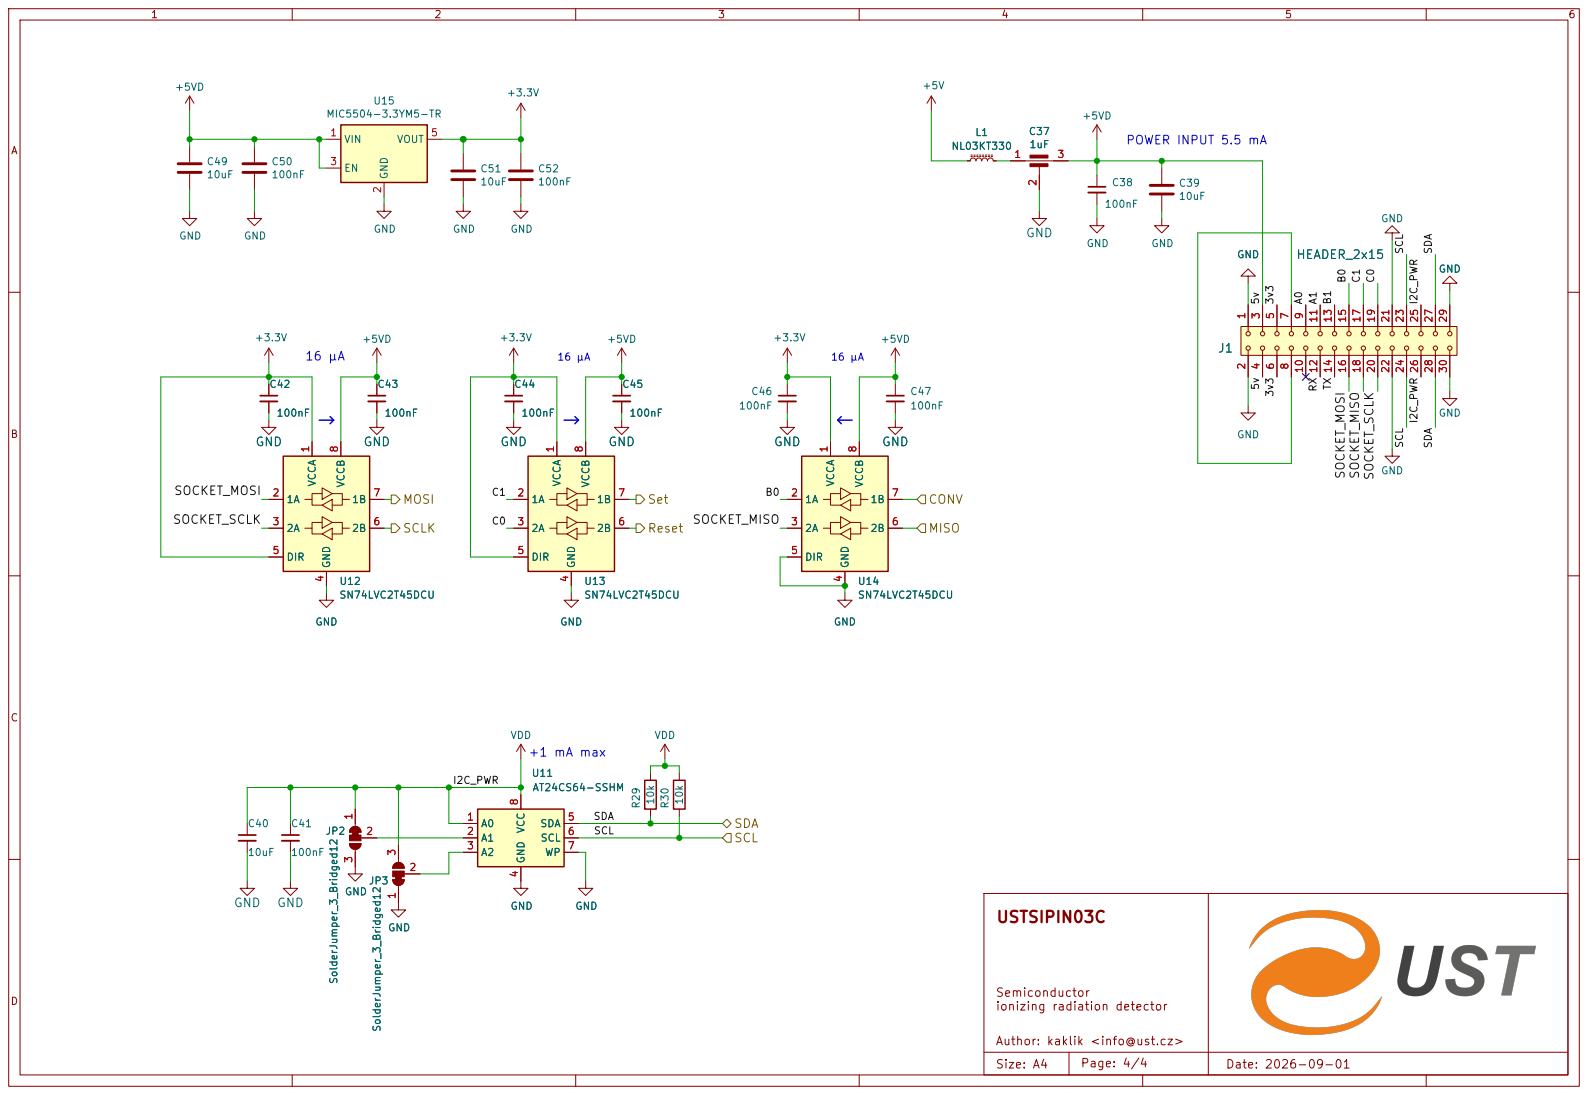
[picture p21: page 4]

USTSIPIN03C Semiconductor ionizing radiation detector Author: kaklik <info@ust.cz>

Size: A4 | Page: 4/4 | Date: 2026-09-01

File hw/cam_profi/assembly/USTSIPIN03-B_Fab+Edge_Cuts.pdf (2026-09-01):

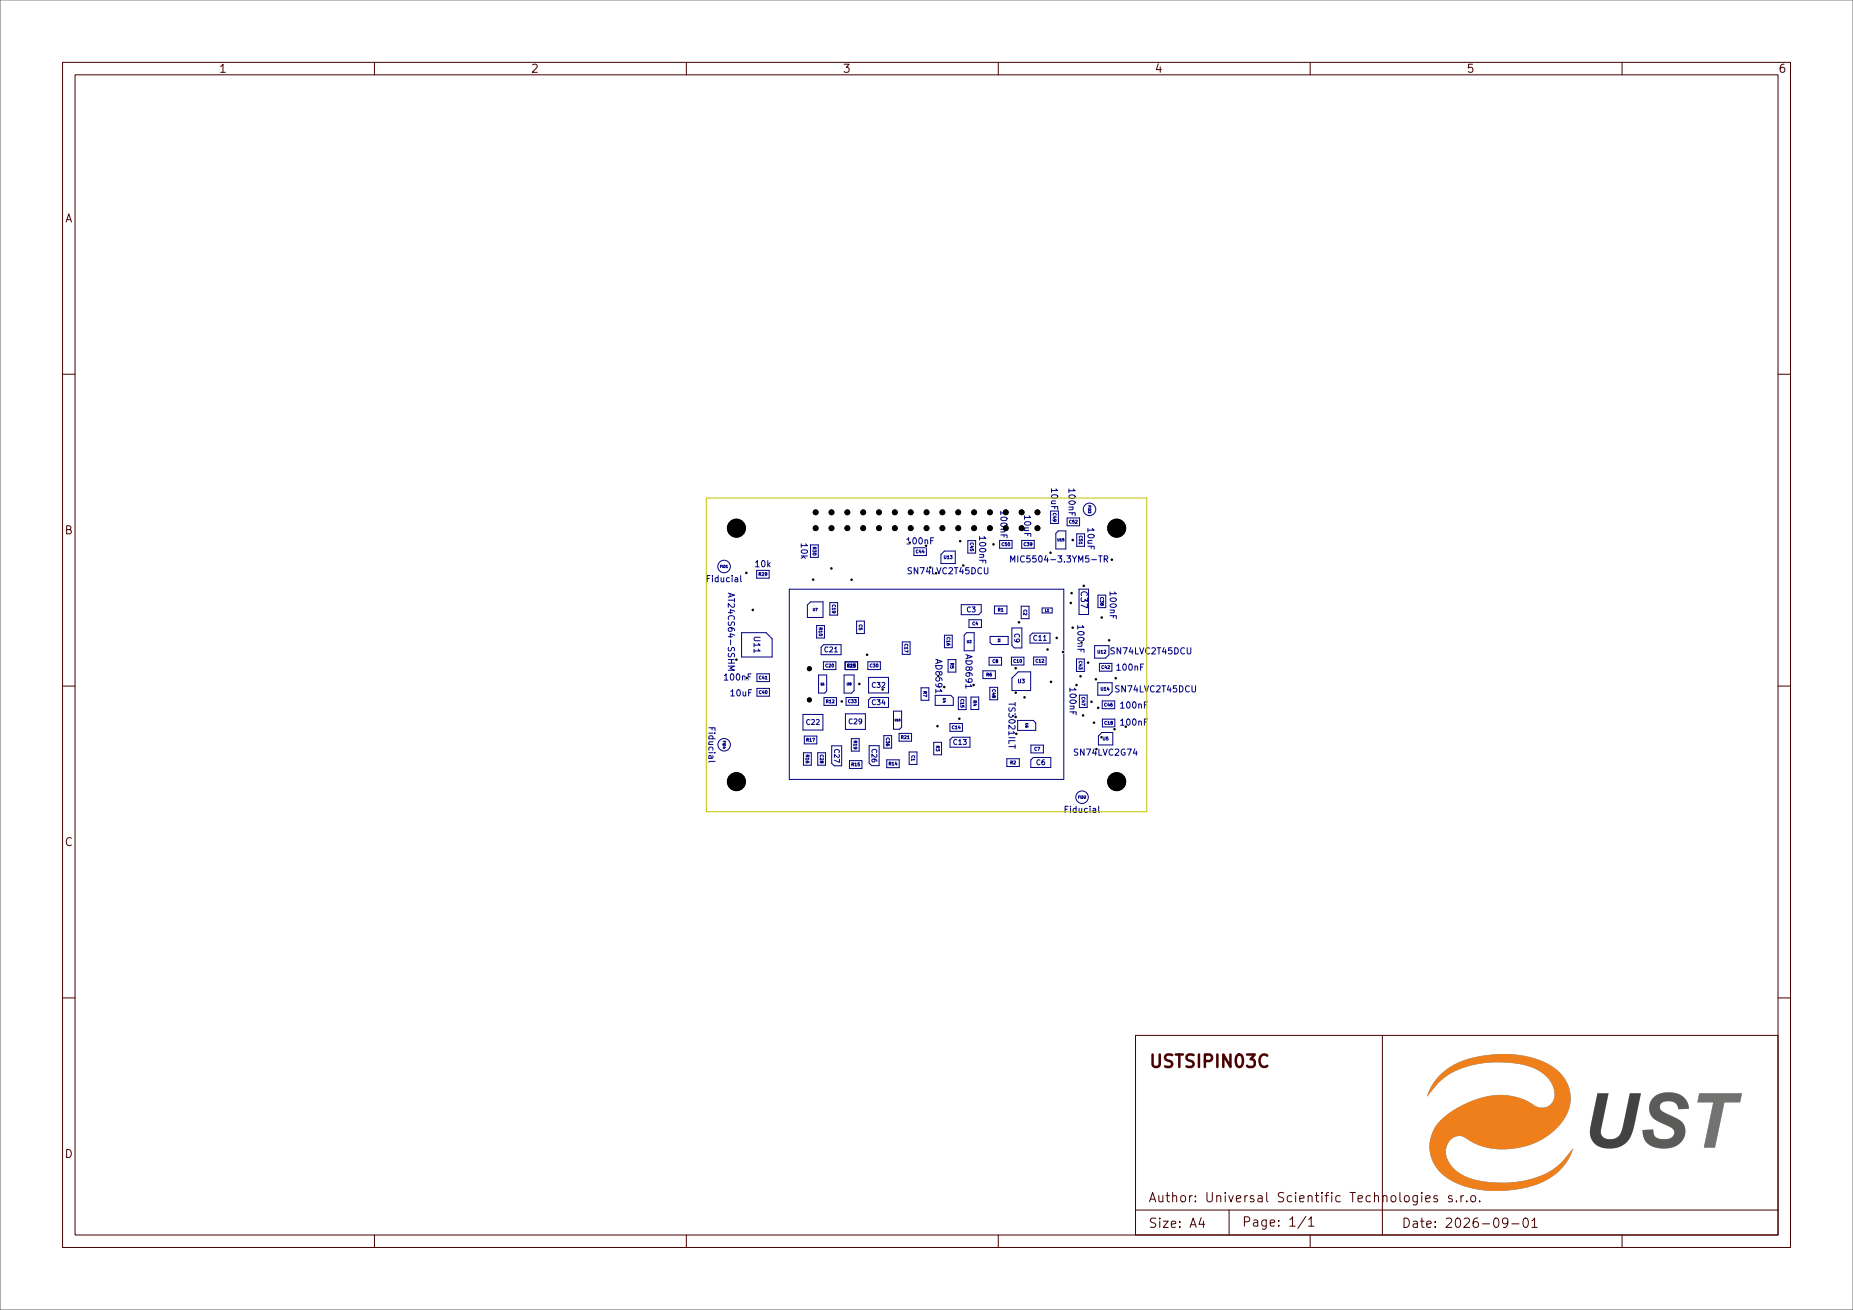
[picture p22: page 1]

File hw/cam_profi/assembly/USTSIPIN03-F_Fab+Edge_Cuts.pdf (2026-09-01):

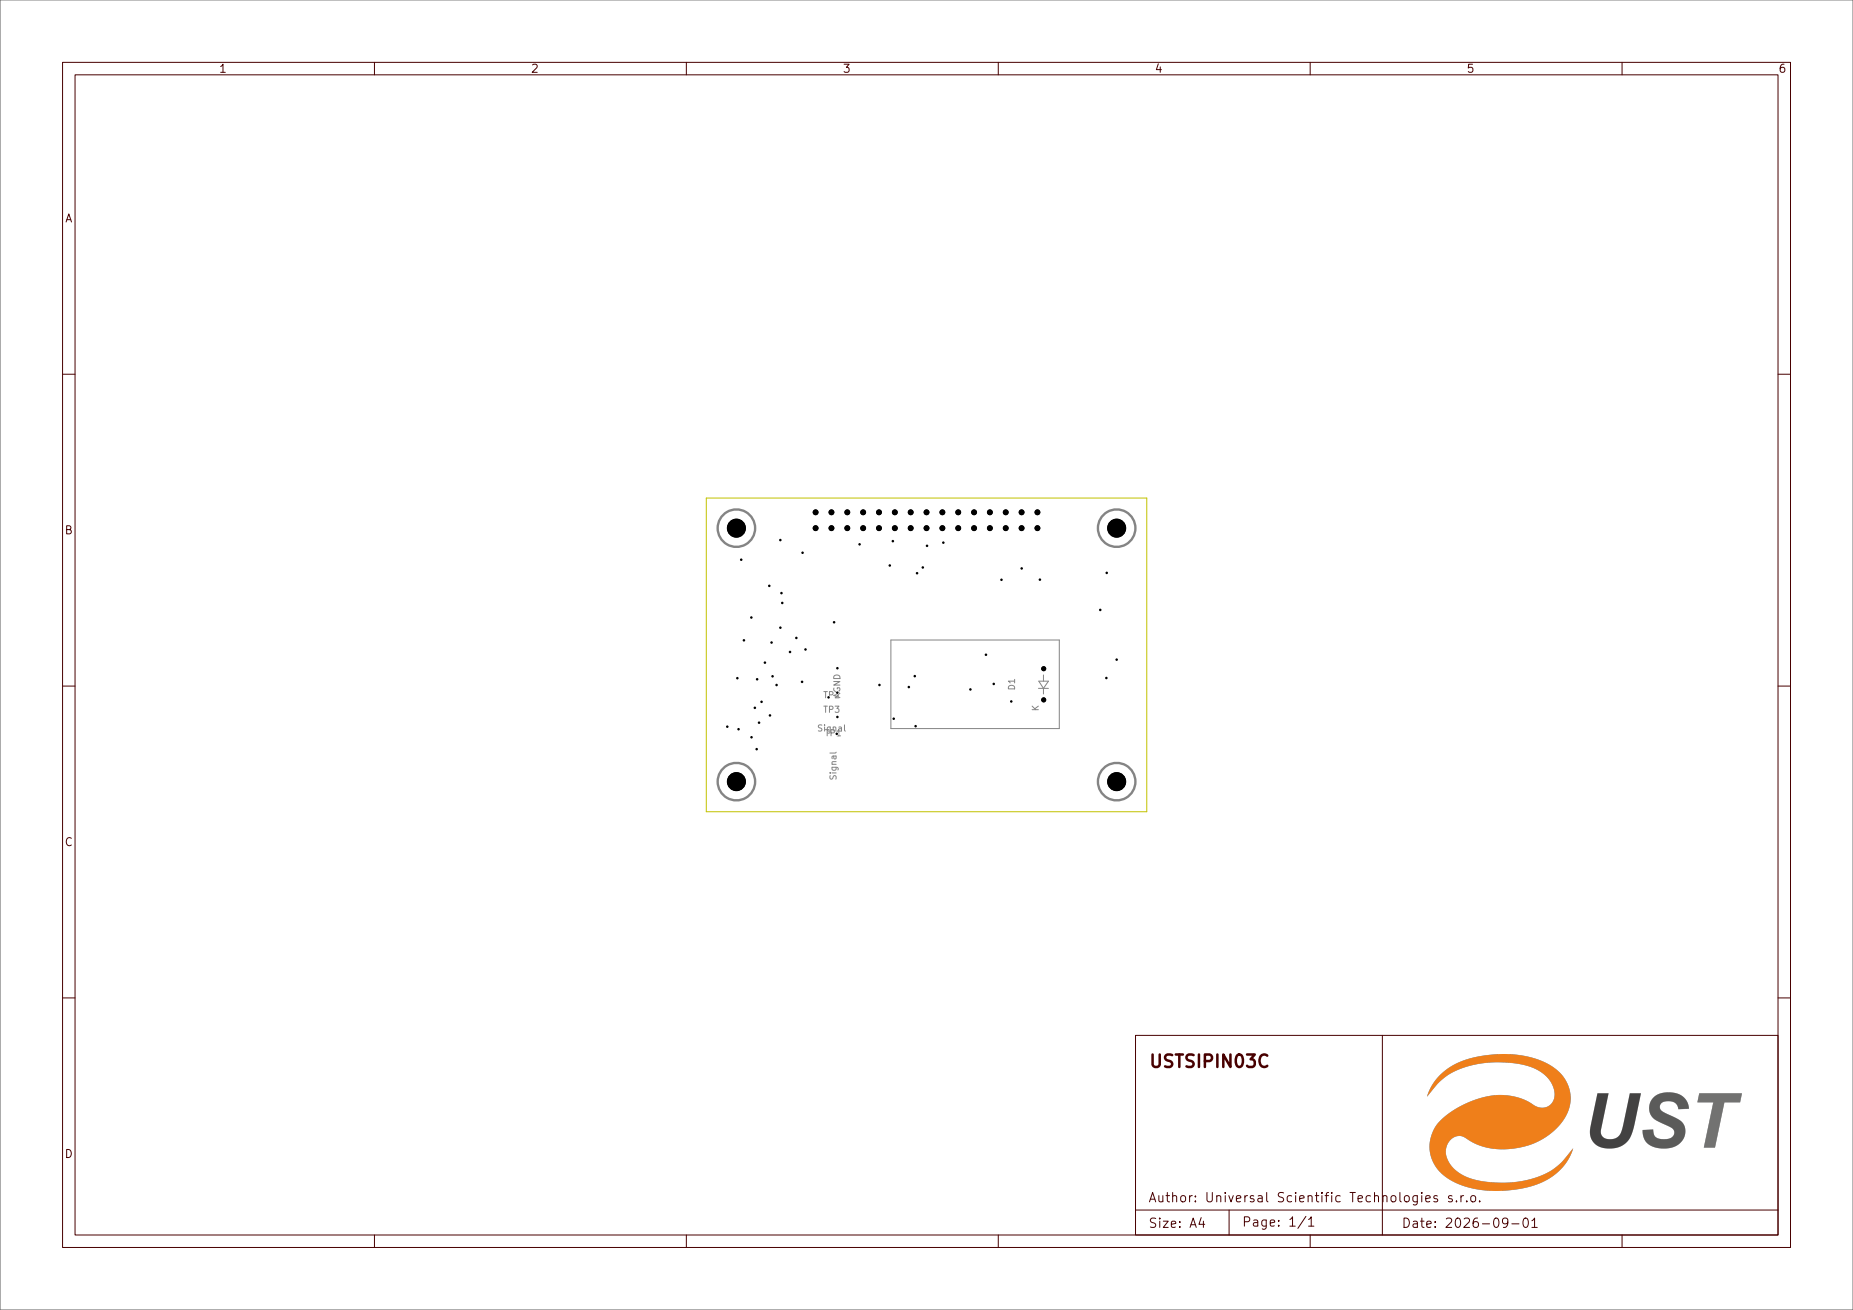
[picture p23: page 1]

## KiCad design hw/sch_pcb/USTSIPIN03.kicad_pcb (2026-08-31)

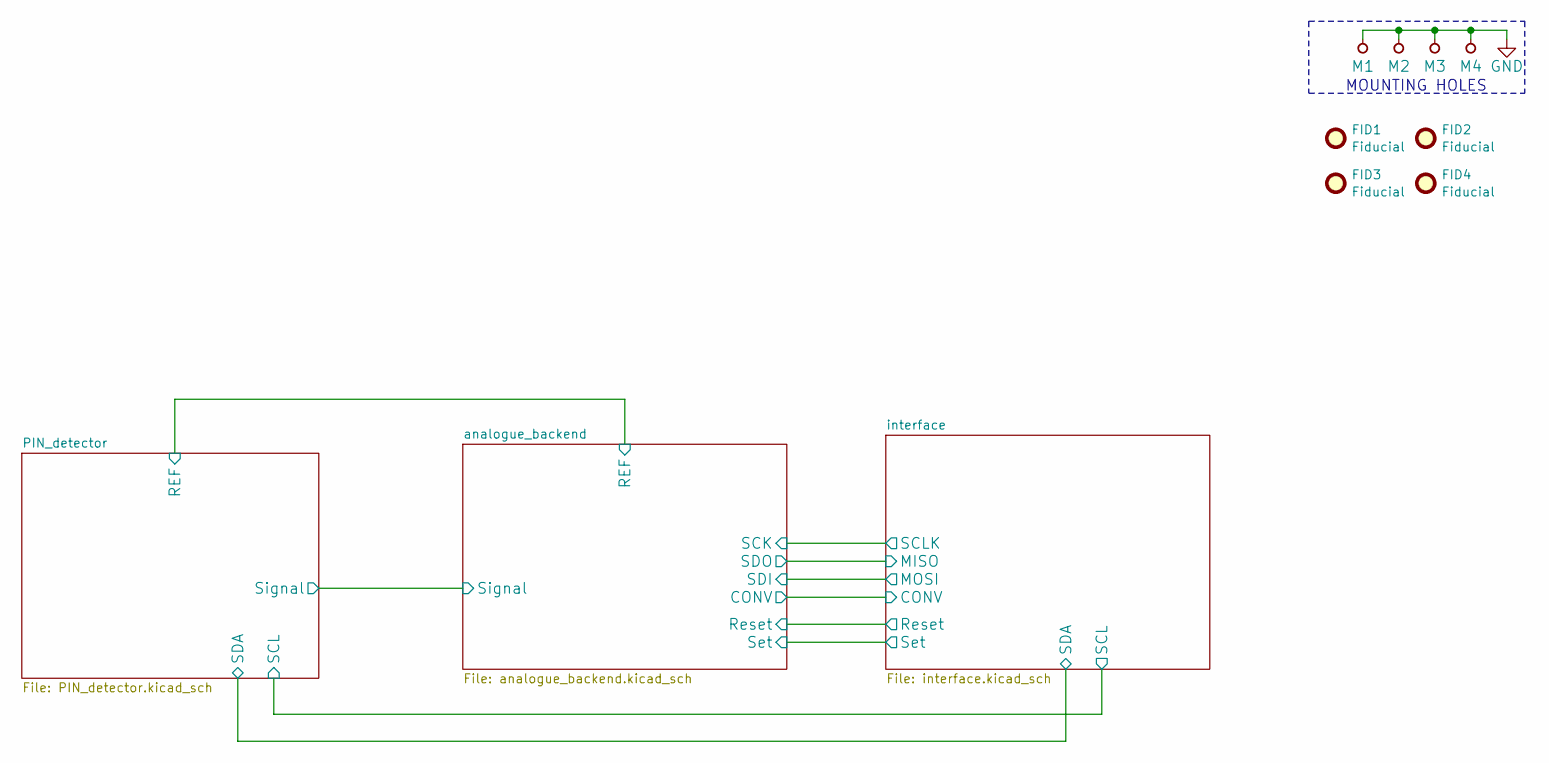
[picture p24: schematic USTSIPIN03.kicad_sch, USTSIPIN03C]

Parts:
FID1, FID2, FID3, FID4: Fiducial; Fiducial_1mm_Mask2mm
M1, M2, M3, M4: HOLE; MountingHole_3mm

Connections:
GND: M1.1, M2.1, M3.1, M4.1; also elsewhere on the board

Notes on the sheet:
MOUNTING HOLES

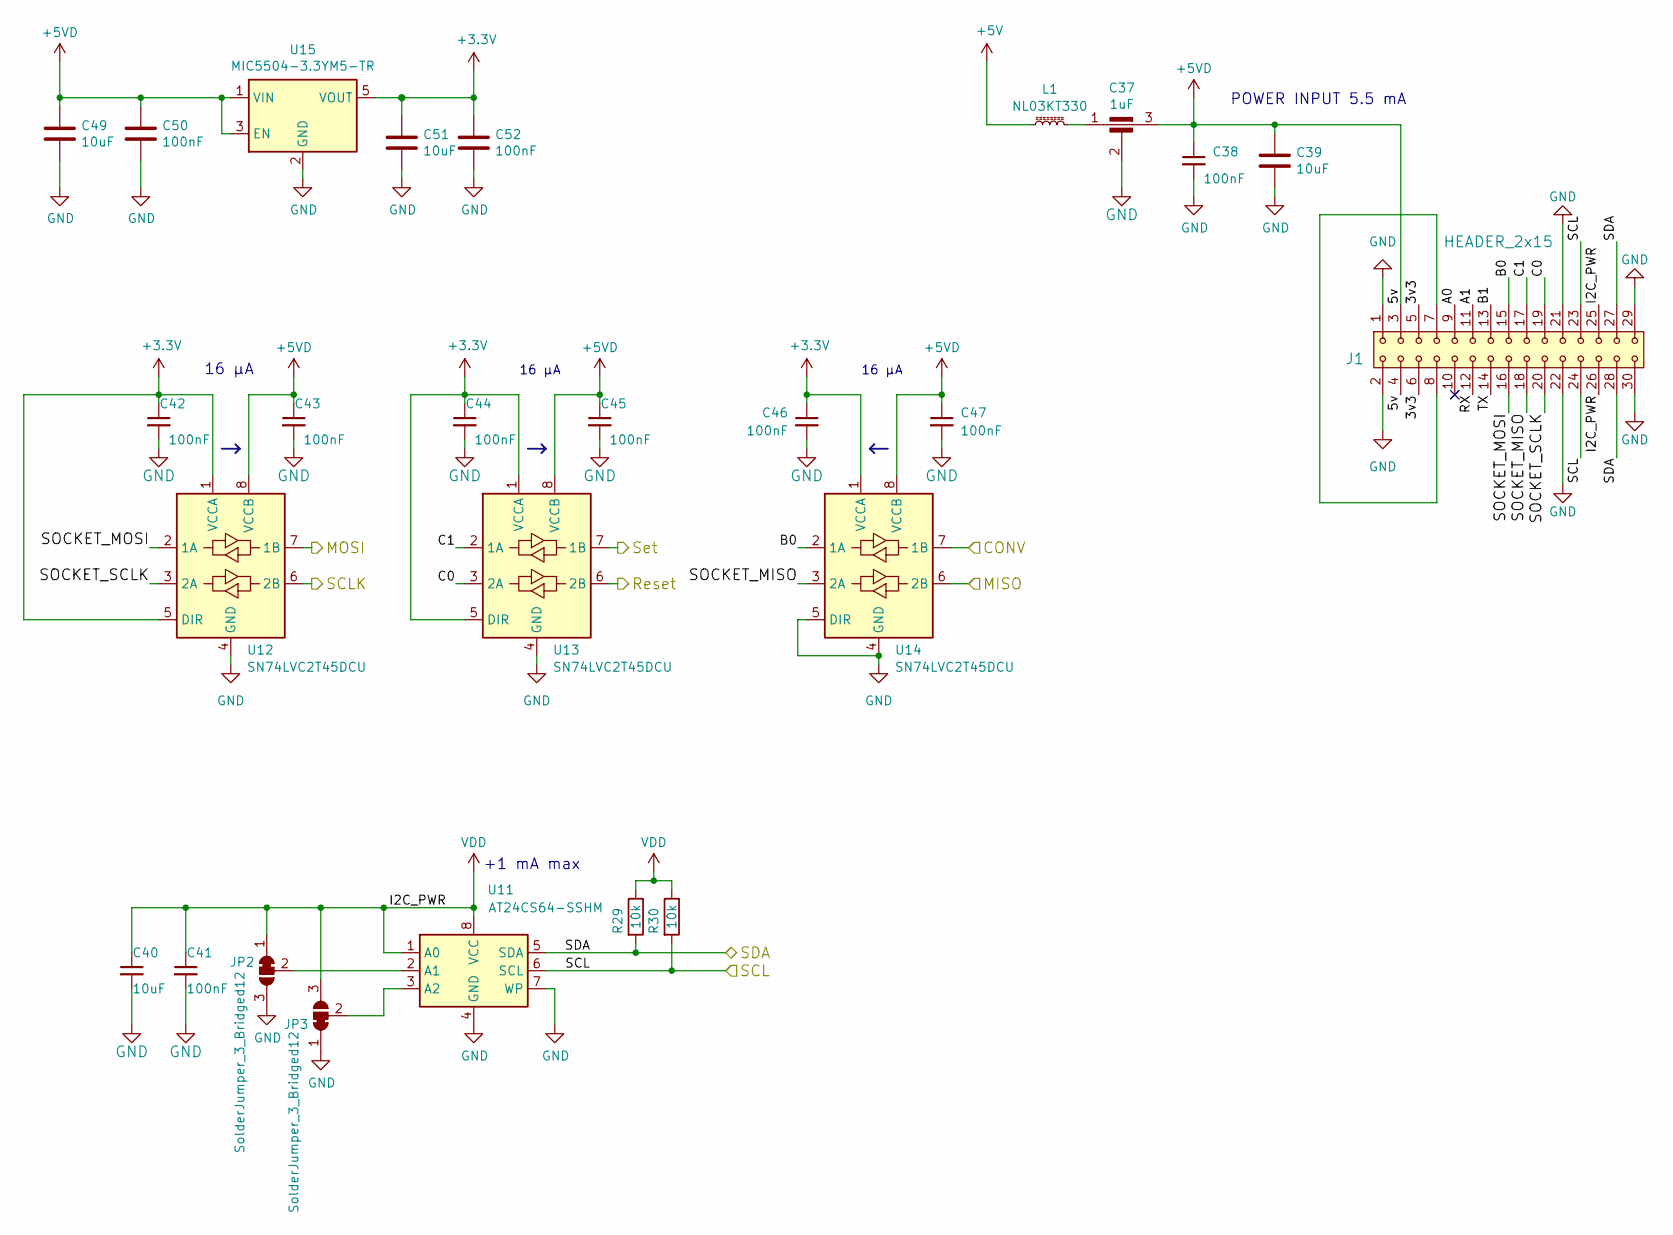
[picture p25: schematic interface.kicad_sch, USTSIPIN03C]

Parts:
C37: 1uF; FIR_0805
C38, C41, C42, C43, C44, C45, C46, C47, C50, C52: 100nF; C_0805_2012Metric
C39, C40, C49, C51: 10uF; C_0805_2012Metric
J1: HEADER_2x15; Straight_2x15
JP2, JP3: SolderJumper_3_Bridged12; SolderJumper-3_P1.3mm_Bridged12_RoundedPad1.0x1.5mm
L1: NL03KT330; L_0603_1608Metric_Pad1.05x0.95mm_HandSolder
R29, R30: 10k; R_0805_2012Metric
U11: AT24CS64-SSHM; SOIC-8_3.9x4.9mm_P1.27mm
U12, U13, U14: SN74LVC2T45DCU; VSSOP-8_2.3x2mm_P0.5mm
U15: MIC5504-3.3YM5-TR; SOT-23-5

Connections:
+3.3V: C42.1, C44.1, C46.1, C51.1, C52.1, U12.1 (VCCA), U12.5 (DIR), U13.1 (VCCA), U13.5 (DIR), U14.1 (VCCA), U15.5 (VOUT)
+5V: L1.1; also elsewhere on the board
+5VD: C37.3, C38.1, C39.1, C43.1, C45.1, C47.1, C49.1, C50.1, J1.3, J1.4, U12.8 (VCCB), U13.8 (VCCB), U14.8 (VCCB), U15.1 (VIN), U15.3 (EN); also elsewhere on the board
/analogue_backend/CONV: U14.7 (1B); also elsewhere on the board
/analogue_backend/Reset: U13.6 (2B); also elsewhere on the board
/analogue_backend/SCK: U12.6 (2B); also elsewhere on the board
/analogue_backend/SDI: U12.7 (1B); also elsewhere on the board
/analogue_backend/SDO: U14.6 (2B); also elsewhere on the board
/analogue_backend/Set: U13.7 (1B); also elsewhere on the board
/interface/3v3: J1.5, J1.6
/interface/A0: J1.9
/interface/A1: J1.11
/interface/B0: J1.15, U14.2 (1A)
/interface/B1: J1.13
/interface/C0: J1.19, U13.3 (2A)
/interface/C1: J1.17, U13.2 (1A)
/interface/RX: J1.12
/interface/SCL: J1.23, J1.24, R30.2, U11.6 (SCL); also elsewhere on the board
/interface/SDA: J1.27, J1.28, R29.2, U11.5 (SDA); also elsewhere on the board
/interface/SOCKET_MISO: J1.18, U14.3 (2A)
/interface/SOCKET_MOSI: J1.16, U12.2 (1A)
/interface/SOCKET_SCLK: J1.20, U12.3 (2A)
/interface/TX: J1.14
GND: C37.2, C38.2, C39.2, C40.2, C41.2, C42.2, C43.2, C44.2, C45.2, C46.2, C47.2, C49.2, C50.2, C51.2, C52.2, J1.1, J1.2, J1.21, J1.22, J1.29, J1.30, JP2.3 (B), JP3.1 (A), U11.4 (GND), U11.7 (WP), U12.4 (GND), U13.4 (GND), U14.4 (GND), U14.5 (DIR), U15.2 (GND); also elsewhere on the board
unnamed: C37.1, L1.2
unnamed: J1.7, J1.8
unnamed: JP2.2 (C), U11.2 (A1)
unnamed: JP3.2 (C), U11.3 (A2)
VDD: C40.1, C41.1, J1.25, J1.26, JP2.1 (A), JP3.3 (B), R29.1, R30.1, U11.1 (A0), U11.8 (VCC); also elsewhere on the board

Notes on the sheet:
+1 mA max
16 μA
POWER INPUT 5.5 mA

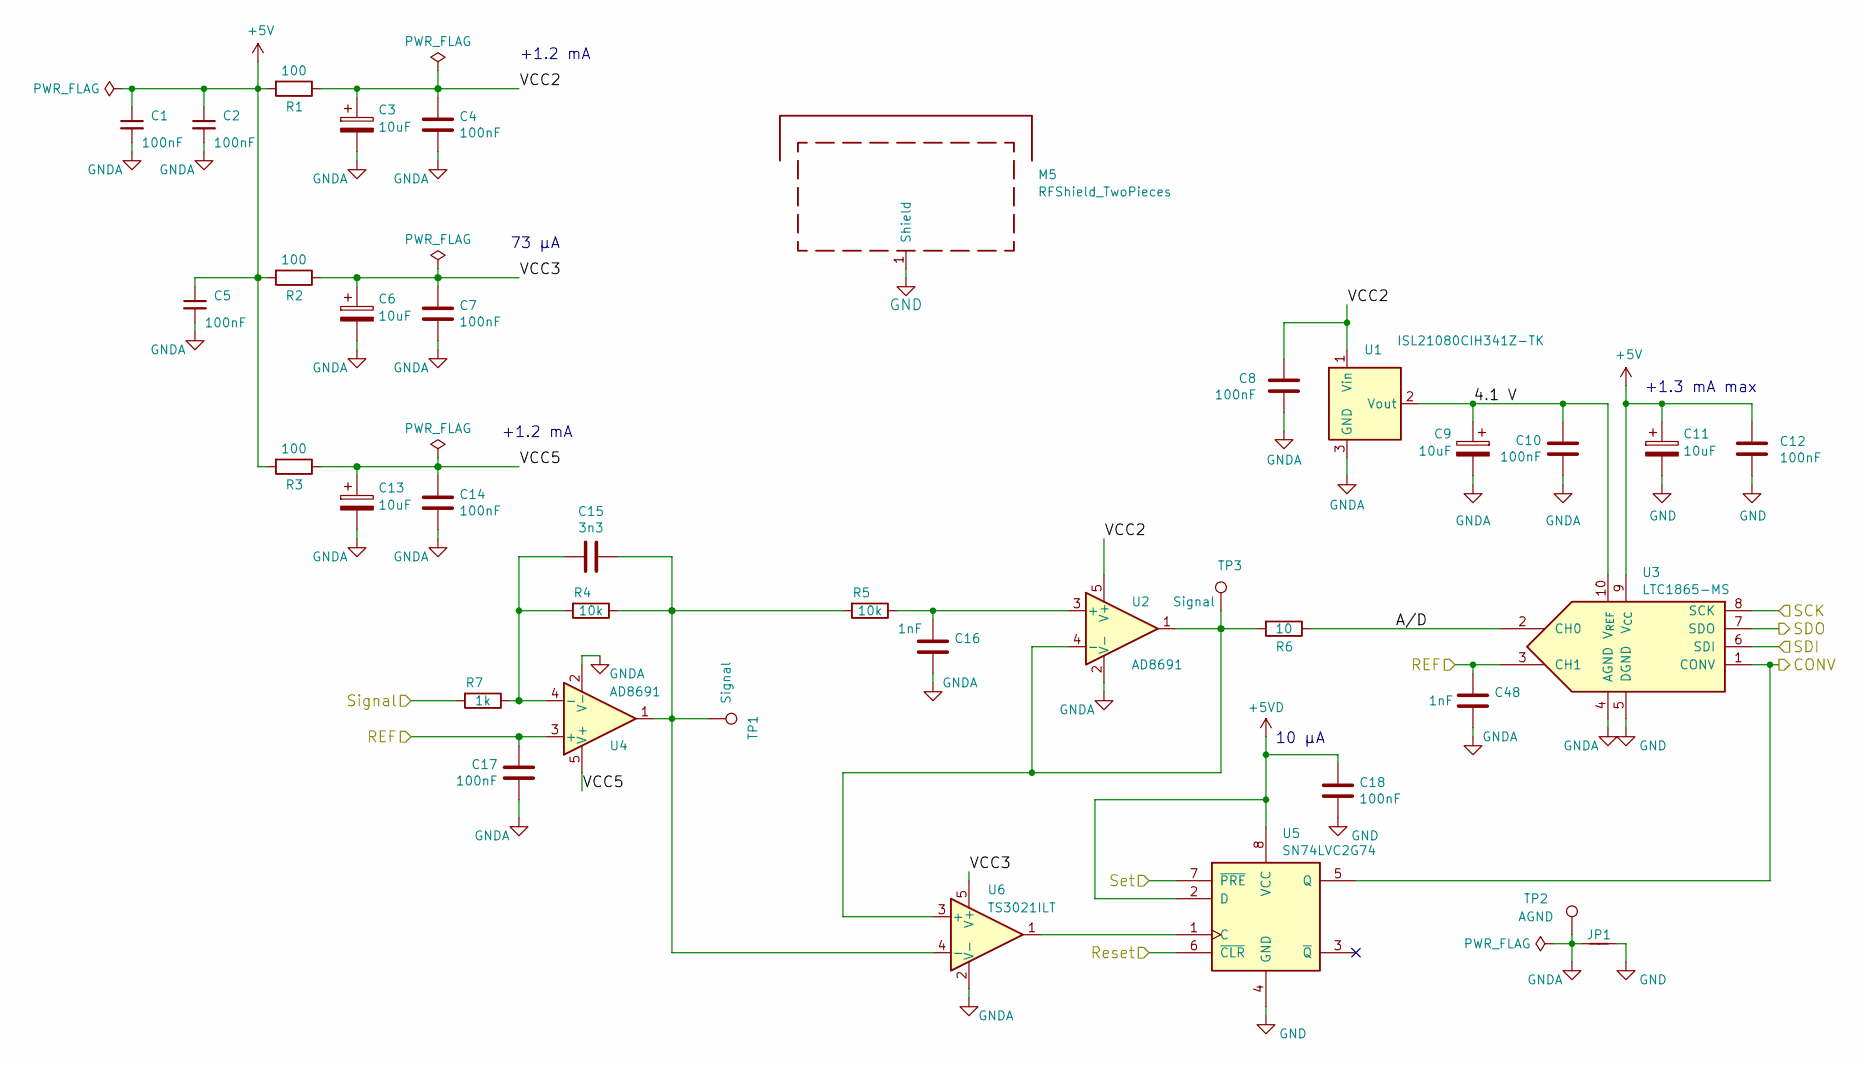
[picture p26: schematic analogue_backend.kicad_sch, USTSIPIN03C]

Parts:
C1, C2, C4, C5, C7, C8, C10, C12, C14, C17, C18: 100nF; C_0805_2012Metric
C3, C6, C9, C11, C13: 10uF; CP_EIA-3216-18_Kemet-A
C15: 3n3; C_0805_2012Metric
C16, C48: 1nF; C_0805_2012Metric
JP1: Jumper_2_Bridged; NetTie-2_SMD_Pad0.5mm
M5: RFShield_TwoPieces; Laird_Technologies_BMI-S-210-F_44.00x30.50mm
R1, R2, R3: 100; R_0805_2012Metric
R4, R5: 10k; R_0805_2012Metric
R6: 10; R_0805_2012Metric
R7: 1k; R_0805_2012Metric
TP1, TP3: Signal; TestPoint_Pad_D1.0mm
TP2: AGND; TestPoint_Pad_D1.0mm
U1: ISL21080CIH341Z-TK; SOT-23
U2, U4: AD8691; TSOT-23-5
U3: LTC1865-MS; MSOP-10_3x3mm_P0.5mm
U5: SN74LVC2G74; VSSOP-8_2.3x2mm_P0.5mm
U6: TS3021ILT; SOT-23-5

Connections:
+5V: C1.1, C2.1, C5.1, C11.1, C12.1, R1.2, R2.2, R3.2, U3.9 (V_{CC}); also elsewhere on the board
+5VD: C18.1, U5.2 (D), U5.8 (VCC); also elsewhere on the board
/PIN_detector/REF: C17.1, C48.1, U3.3 (CH1), U4.3 (+); also elsewhere on the board
/PIN_detector/Signal: R7.2; also elsewhere on the board
/analogue_backend/4.1 V: C9.1, C10.1, U1.2 (Vout), U3.10 (V_{REF})
/analogue_backend/A/D: R6.1, U3.2 (CH0)
/analogue_backend/CONV: U3.1 (CONV), U5.5 (Q); also elsewhere on the board
/analogue_backend/Reset: U5.6 (~CLR); also elsewhere on the board
/analogue_backend/SCK: U3.8 (SCK); also elsewhere on the board
/analogue_backend/SDI: U3.6 (SDI); also elsewhere on the board
/analogue_backend/SDO: U3.7 (SDO); also elsewhere on the board
/analogue_backend/Set: U5.7 (~PRE); also elsewhere on the board
/analogue_backend/VCC2: C3.1, C4.1, C8.1, R1.1, U1.1 (Vin), U2.5 (V+)
/analogue_backend/VCC3: C6.1, C7.1, R2.1, U6.5 (V+)
/analogue_backend/VCC5: C13.1, C14.1, R3.1, U4.5 (V+)
GND: C11.2, C12.2, C18.2, JP1.2, M5.1 (Shield), U3.5 (DGND), U5.4 (GND); also elsewhere on the board
GNDA: C1.2, C2.2, C3.2, C4.2, C5.2, C6.2, C7.2, C8.2, C9.2, C10.2, C13.2, C14.2, C16.2, C17.2, C48.2, JP1.1, TP2.1, U1.3 (GND), U2.2 (V-), U3.4 (AGND), U4.2 (V-), U6.2 (V-); also elsewhere on the board
unnamed: C16.1, R5.1, U2.3 (+)
unnamed: R6.2, TP3.1, U2.1, U2.4 (-), U6.3 (+)
unnamed: C15.2, R4.2, R7.1, U4.4 (-)
unnamed: U5.1 (C), U6.1
unnamed: C15.1, R4.1, R5.2, TP1.1, U4.1, U6.4 (-)

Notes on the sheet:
+1.3 mA max
+1.2 mA
73 μA
10 μA

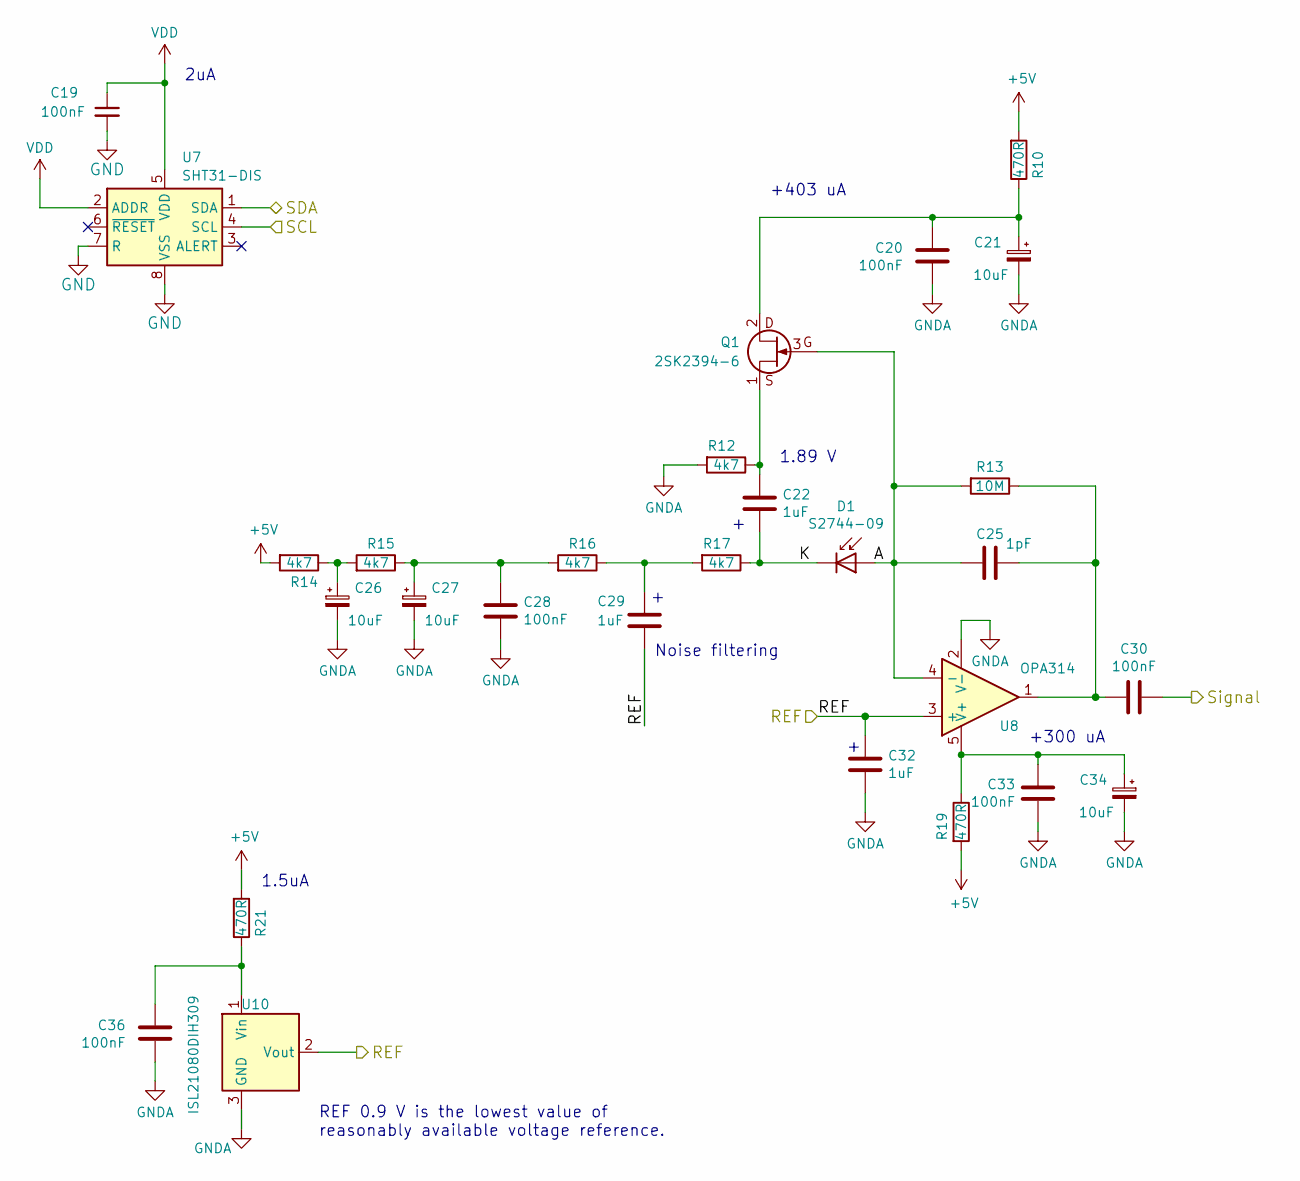
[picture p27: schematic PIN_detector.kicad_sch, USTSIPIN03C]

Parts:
C19, C20, C28, C30, C33, C36: 100nF; C_0805_2012Metric
C21, C26, C27, C34: 10uF; CP_EIA-3216-18_Kemet-A
C22, C29, C32: 1uF; C_1210_3225Metric
C25: 1pF; C_0805_2012Metric
D1: S2744-09; HAMAMATSU_S2744-09
Q1: 2SK2394-6; SOT-23
R10, R19, R21: 470R; R_0805_2012Metric
R12, R14, R15, R16, R17: 4k7; R_0805_2012Metric
R13: 10M; R_0805_2012Metric
U7: SHT31-DIS; Sensirion_DFN-8-1EP_2.5x2.5mm_P0.5mm_EP1.1x1.7mm
U8: OPA314; SOT-23-5
U10: ISL21080DIH309; SOT-23

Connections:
+5V: R10.2, R14.2, R19.2, R21.2; also elsewhere on the board
/PIN_detector/A: C25.2, D1.2 (A), Q1.3 (G), R13.2, U8.4 (-)
/PIN_detector/K: C22.2, D1.1 (K), R17.1
/PIN_detector/REF: C29.2, C32.1, U8.3 (+), U10.2 (Vout); also elsewhere on the board
/PIN_detector/Signal: C30.1; also elsewhere on the board
/interface/SCL: U7.4 (SCL); also elsewhere on the board
/interface/SDA: U7.1 (SDA); also elsewhere on the board
GND: C19.2, U7.7 (R), U7.8 (VSS), U7.9 (VSS); also elsewhere on the board
GNDA: C20.2, C21.2, C26.2, C27.2, C28.2, C32.2, C33.2, C34.2, C36.2, R12.2, U8.2 (V-), U10.3 (GND); also elsewhere on the board
unnamed: C25.1, C30.2, R13.1, U8.1
unnamed: C26.1, R14.1, R15.2
unnamed: C27.1, C28.1, R15.1, R16.2
unnamed: C29.1, R16.1, R17.2
unnamed: C20.1, C21.1, Q1.2 (D), R10.1
unnamed: C22.1, Q1.1 (S), R12.1
unnamed: C33.1, C34.1, R19.1, U8.5 (V+)
unnamed: C36.1, R21.1, U10.1 (Vin)
VDD: C19.1, U7.2 (ADDR), U7.5 (VDD); also elsewhere on the board

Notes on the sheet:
1.89 V
2uA
Noise filtering
REF 0.9 V is the lowest value of reasonably available voltage reference.
1.5uA
+300 uA
+403 uA

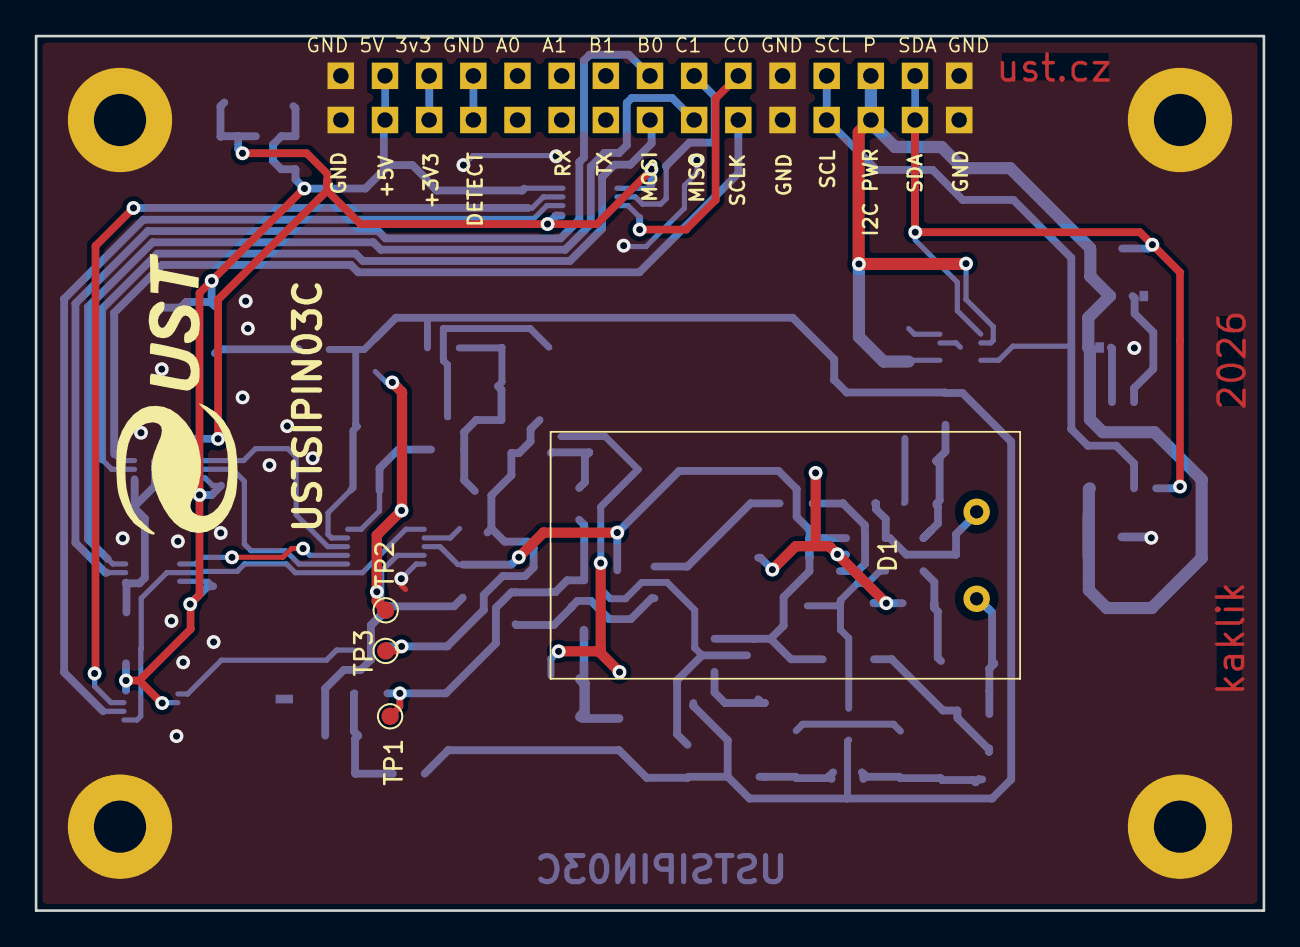
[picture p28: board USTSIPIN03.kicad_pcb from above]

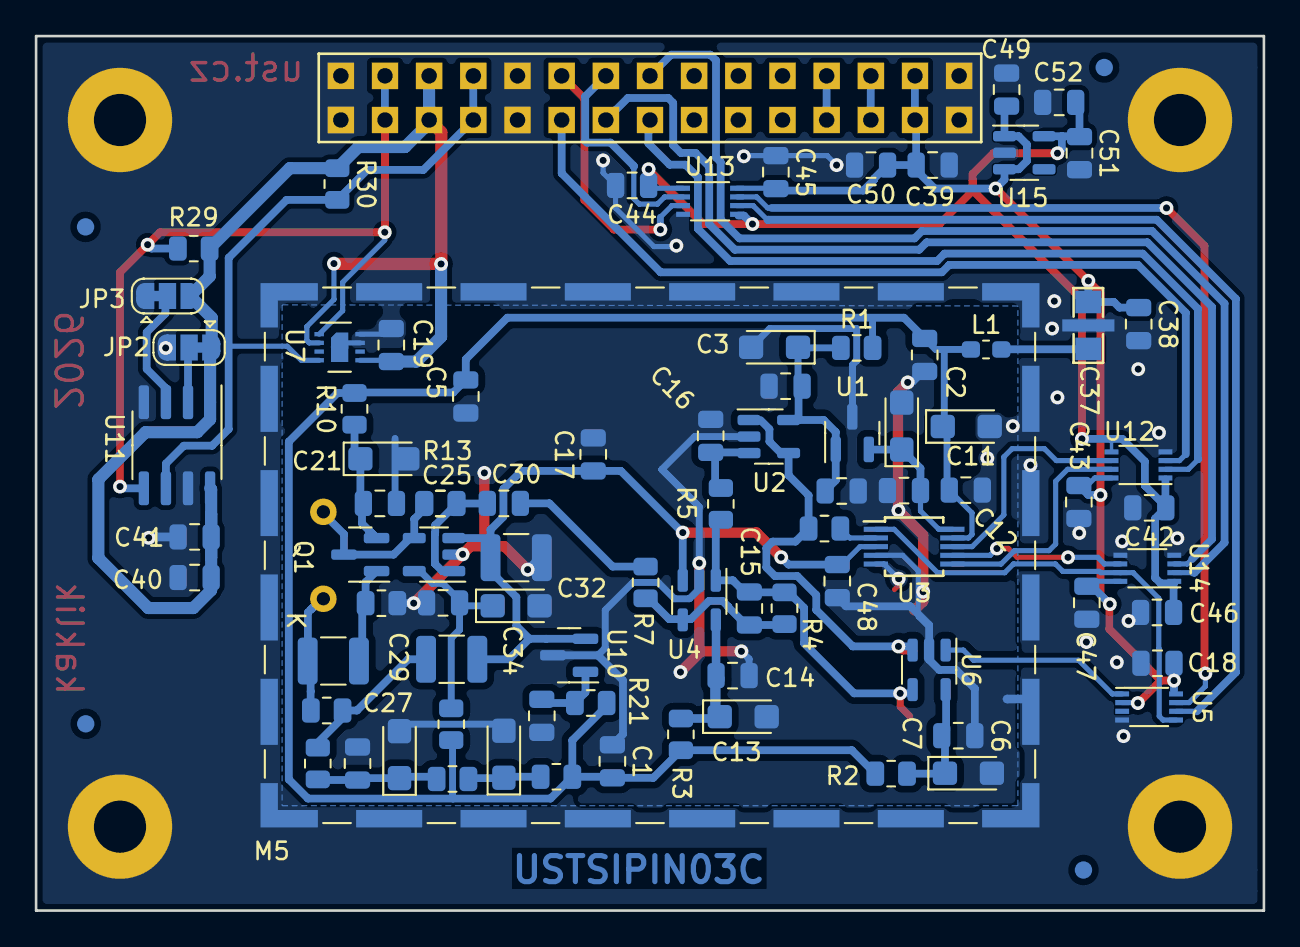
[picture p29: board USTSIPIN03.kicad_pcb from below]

Board: 2 copper layers, 70.6 x 50.3 mm, 100 parts (91 on the bottom side), 47 nets.

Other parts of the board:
G1: LOGO; UST

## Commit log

2025-02-15 Update project to KiCADv8.
    [PIN_detector.kicad_sch, USTSIPIN03.kicad_pcb, USTSIPIN03.kicad_sch, analogue_backend.kicad_sch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]
2025-02-15 Update actions products
    [USTSIPIN03-B_Courtyard.dxf, USTSIPIN03-B_Cu.dxf, USTSIPIN03-B_Fab.dxf, USTSIPIN03-B_Mask.dxf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]
2025-02-15 Fix #8 Adding solder jumpers.
    [USTSIPIN03.kicad_pcb, interface.kicad_sch]
2025-02-16 Resolve #10
    [PIN_detector.kicad_sch, USTSIPIN03.kicad_pcb, USTSIPIN03.kicad_sch, analogue_backend.kicad_sch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]
2025-02-16 Improve layout.
    [USTSIPIN03.kicad_pcb]
2025-03-02 Cleanup Fab layer.
    [USTSIPIN03.kicad_pcb]
2025-04-26 Fix wrong revision in silkscreen.
    [USTSIPIN03.kicad_pcb]
2025-05-05 Update UST_ID for ADC.
    [USTSIPIN03.kicad_pcb, analogue_backend.kicad_sch]
2026-01-16 Update KiCAD project.
    [PIN_detector.kicad_sch, USTSIPIN03.kicad_pcb, USTSIPIN03.kicad_sch, analogue_backend.kicad_sch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]
2026-01-21 Add dimensioned drawing.
    [USTSIPIN03.kicad_pcb]
2026-03-06 Add modified version of sensor frame.
    [sensor_frame.3mf, sensor_frame.scad, sensor_frame.stl]

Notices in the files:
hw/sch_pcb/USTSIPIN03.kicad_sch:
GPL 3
